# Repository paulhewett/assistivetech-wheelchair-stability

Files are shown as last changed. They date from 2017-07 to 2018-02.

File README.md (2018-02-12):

## Wheelchair Static Stability Test Rig

This system can be sued to measure wheelchair static stability. The design's being published to allow better community development and feedback.

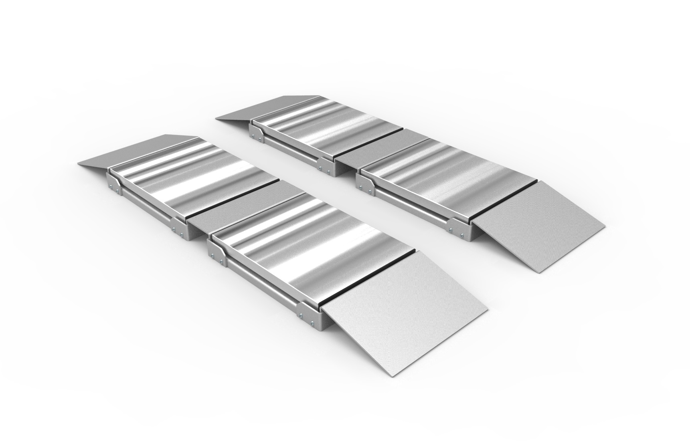
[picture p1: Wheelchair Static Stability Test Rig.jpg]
Wheelchair Static Stability Test Rig


You can use [these pages to see the instructions and to calculate theoretical stability](https://paulhewett.github.io/wheelchair-static-stability-test-rig/) based on scale measurement data.

I've currently just posted a version developed some years ago, with a view to some development soon. It is still a work in progress, so do bear with!

The hardware design will be published, and is similar to the version shown in the photos. We are currently working with digital scales, and I do use the calculation form.

If you do use it, you will need to establish your own protocol for best practice. The formulae used need checking, so check them first before you rely on them. 

Also see these two related repositories:

https://github.com/ACECentre/MAT-doc

https://github.com/ACECentre/Wheelchair-Stability-App

Development is happening now, so get in touch or add issues to feed into this project. Thanks!

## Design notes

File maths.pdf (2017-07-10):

WHEELCHAIR STABILITY MEASUREMENT SYSTEM

Considering the diagram below to find the total weight:

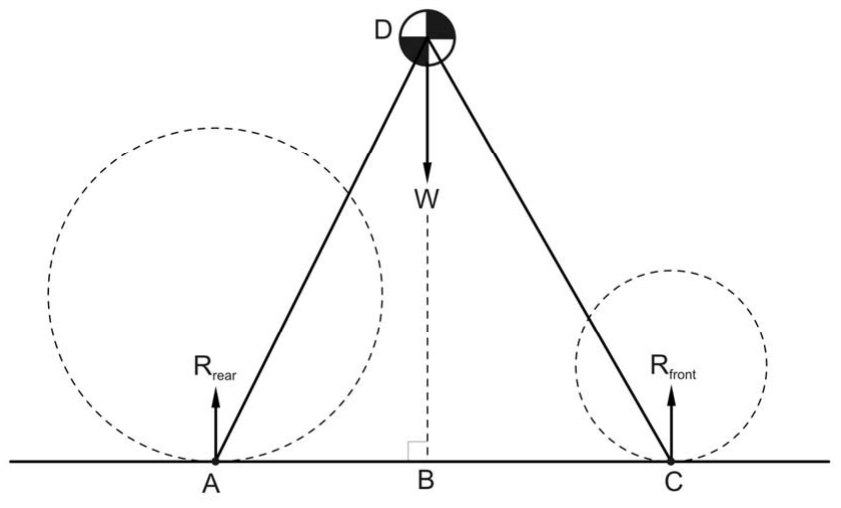
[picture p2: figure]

Rrear = Massrear x 9.81

Rfront = Massfront x 9.81

W = Rrear + Rfront

Considering the following diagram:

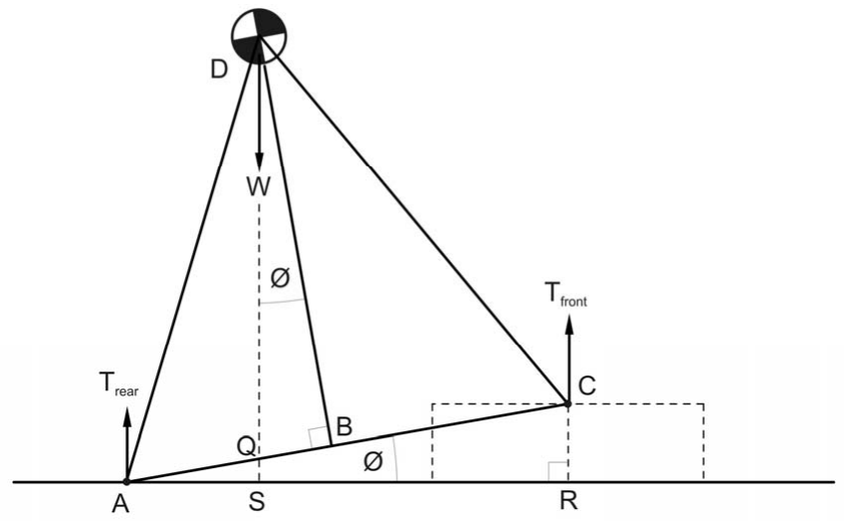
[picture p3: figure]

Taking moments about A to find AB:

AB x W = AC x Rfront

AB = (AC x Rfront) / W

Also,

sin ø = CR/AC

ø = arcsin (CR/AC)

The mass on one pair of wheels is measured to provide an angle of tip.

Tfront = Mfront x 9.81

To find AR:

cos ø = AR/AC

AR = AC x cos ø

Taking moments about A to find AS:

AS x W = AR x Tfront

AS = (AR x Tfront) / W

To find AQ:

cos ø = AS / AQ

AQ = AS / cos ø

To find BQ:

AB = AQ + BQ

BQ = AB – AQ

To find BD:

tan ø = BQ / BD

BD = BQ / tan ø

Consider the following diagram to find the tip and the maximum kerb height

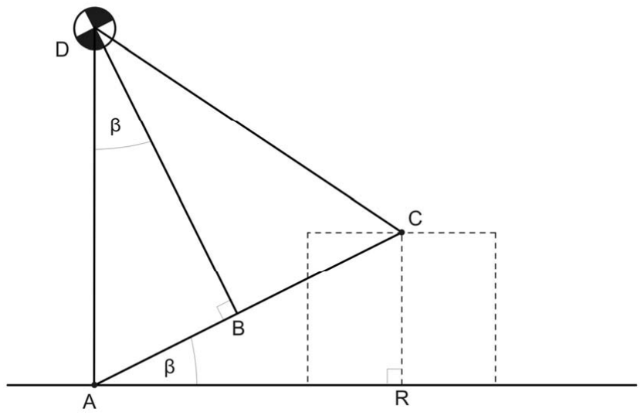
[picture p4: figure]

To find the angle of tip in a rearward direction:

tan β = AB / BD

β = arctan (AB / BD)

To find maximum height of kerb:

sin β = CR / AC

CR = AC sin β

To find the angle of tip in a forward direction:

tan δ = BC / BD

δ = arctan (BC / BD)

To find the maximum height of kerb:

sin δ = AR / AC

AR = AC sin δ

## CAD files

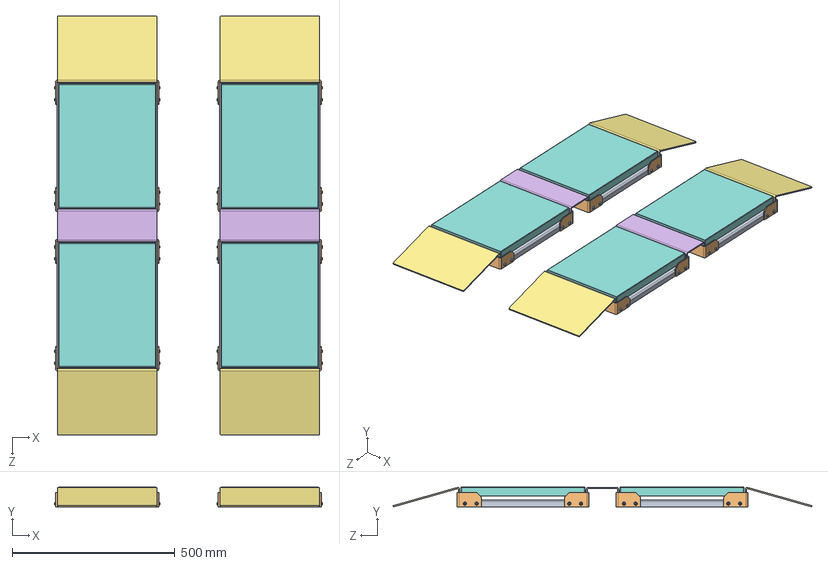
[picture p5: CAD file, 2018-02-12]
CAD/303-001 Test Rig Assembly/303-001-001 Test Rig Asembly.SLDASM
824.6 x 61.0 x 1288.2 mm
M6x16 Allen Button Head Screw x 32
M6 Washer Plain x 32
Nyloc Nut x 32
Salter WS120 Scales x 4

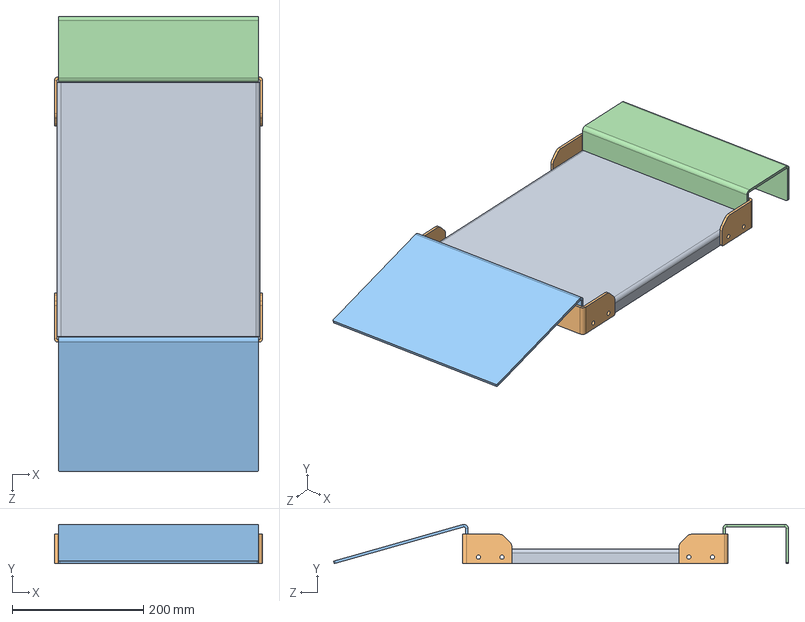
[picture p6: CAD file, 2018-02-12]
CAD/303-005 Assembly/303-005-001.SLDASM
318.0 x 60.0 x 694.1 mm

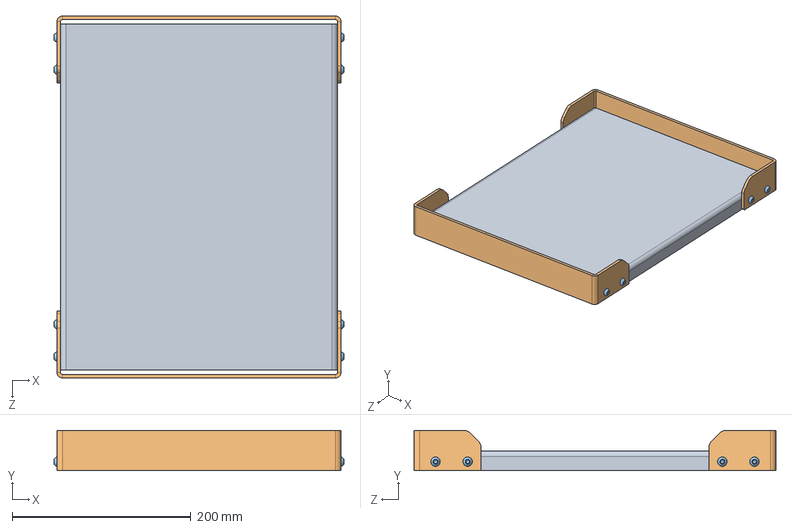
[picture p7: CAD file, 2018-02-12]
CAD/303-005 Assembly/303-005-002.SLDASM
324.6 x 45.0 x 405.0 mm
M6x16 Allen Button Head Screw x 8
M6 Washer Plain x 8
Nyloc Nut x 8

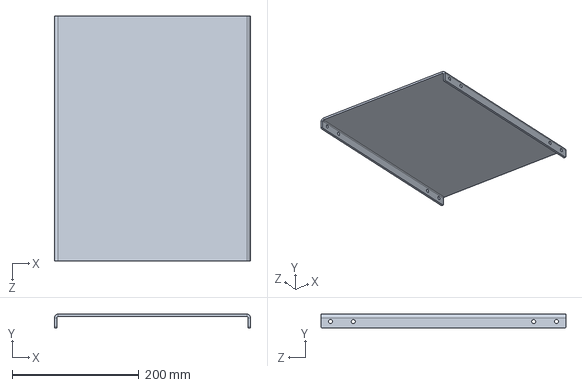
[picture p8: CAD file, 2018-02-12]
CAD/303-002 Scale Platform/303-002-001.SLDPRT
310.0 x 22.0 x 387.0 mm

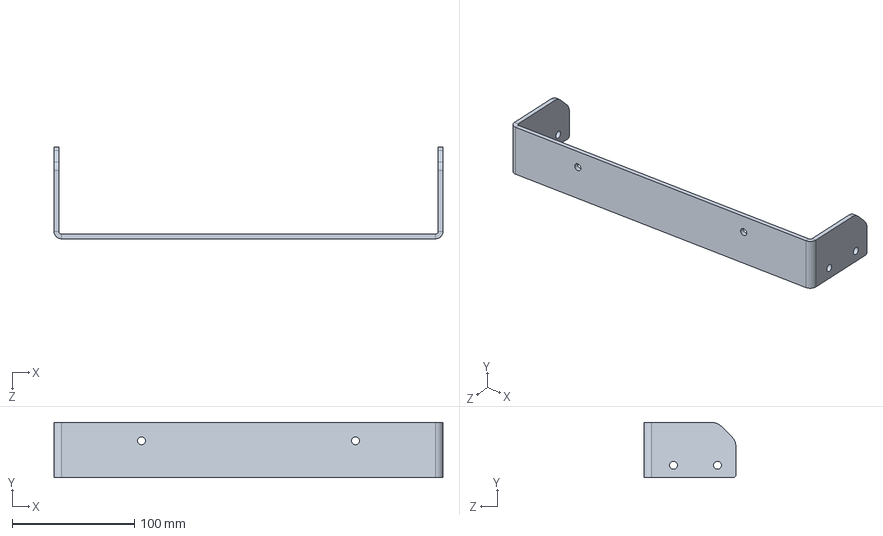
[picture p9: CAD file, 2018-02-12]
CAD/303-003 End Guide/303-003-001.SLDPRT
318.0 x 45.0 x 75.0 mm

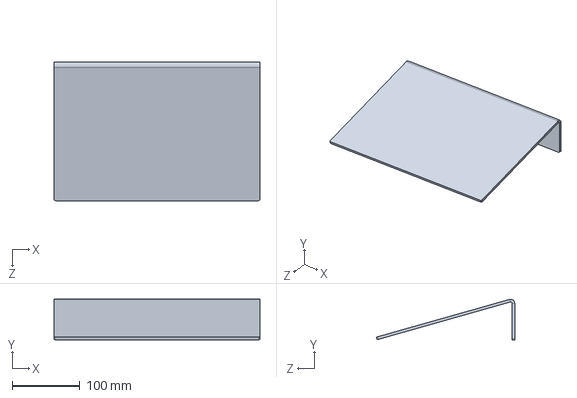
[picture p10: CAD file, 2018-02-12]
CAD/303-004 Ramp/303-004-001.SLDPRT
305.0 x 60.0 x 205.1 mm

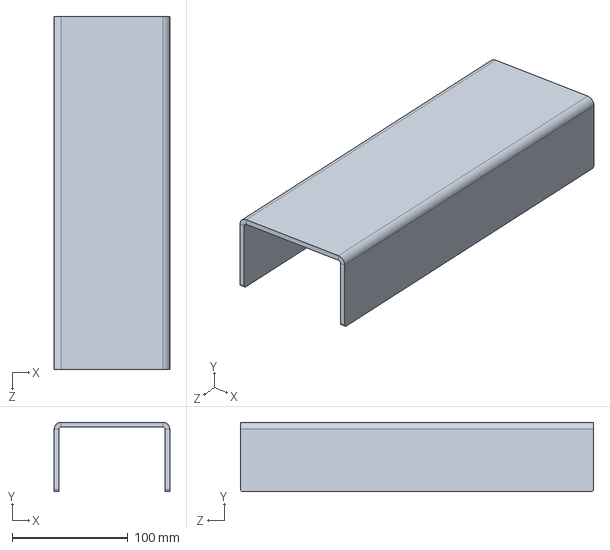
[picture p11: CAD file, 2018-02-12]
CAD/303-006 Spacer Plate/303-006-002.SLDPRT
100.0 x 60.0 x 305.0 mm

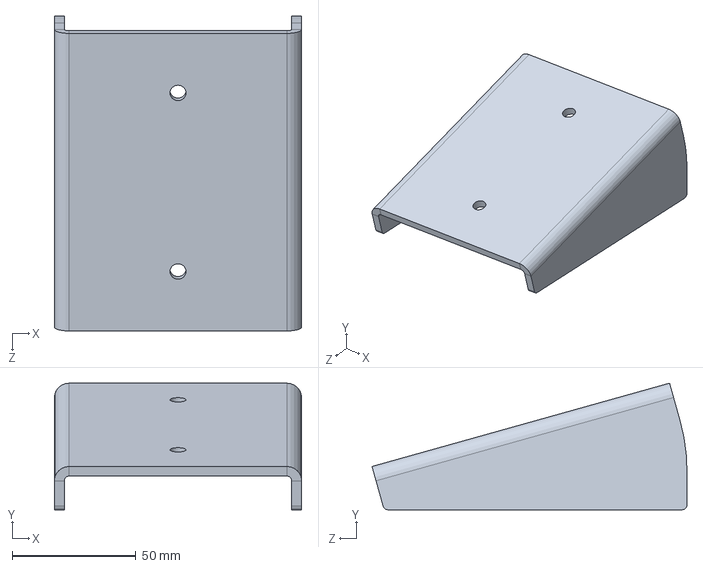
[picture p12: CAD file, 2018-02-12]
CAD/303-007 Ramp Support/303-007-001.SLDPRT
100.0 x 51.2 x 127.4 mm

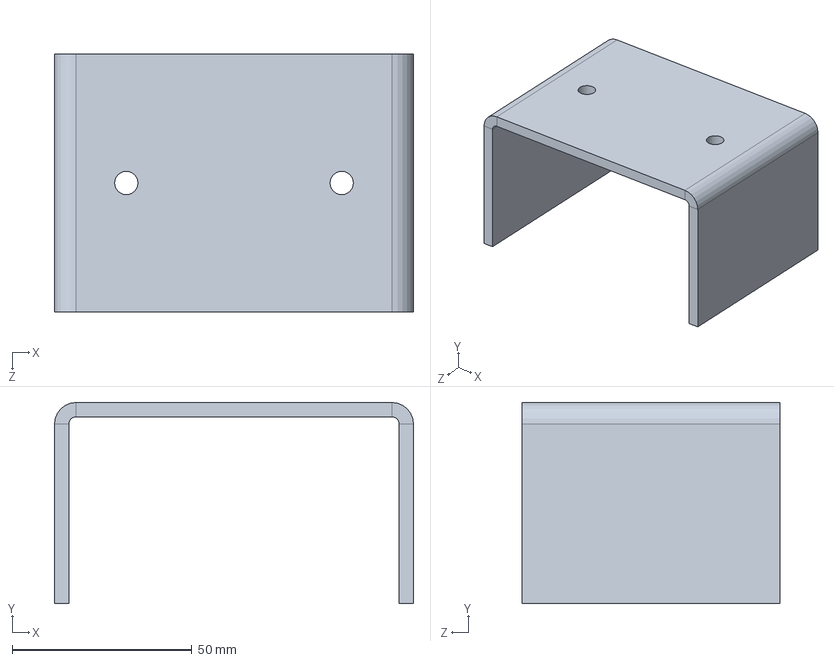
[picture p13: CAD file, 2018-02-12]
CAD/303-008 Support Plate/303-008-001.SLDPRT
100.0 x 56.0 x 72.0 mm

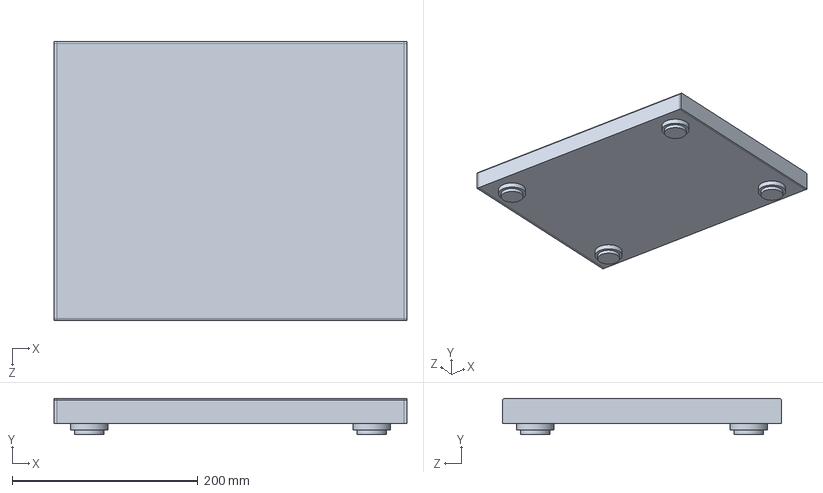
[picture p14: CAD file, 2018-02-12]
CAD/_parts/Salter WS120 Scales.SLDPRT
380.0 x 39.0 x 300.0 mm

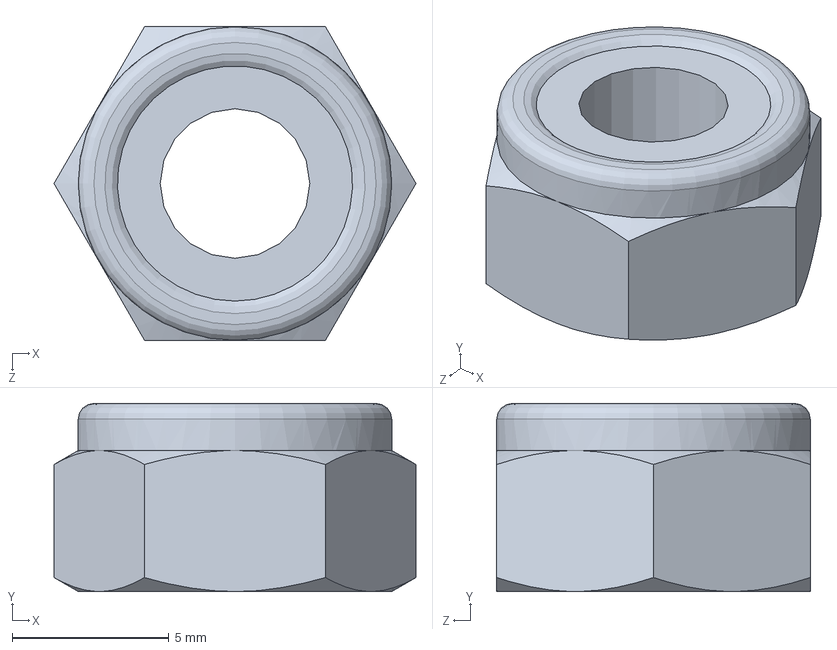
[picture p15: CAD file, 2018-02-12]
CAD/_parts/Nyloc Nut.SLDPRT
11.5 x 6.00 x 10.0 mm

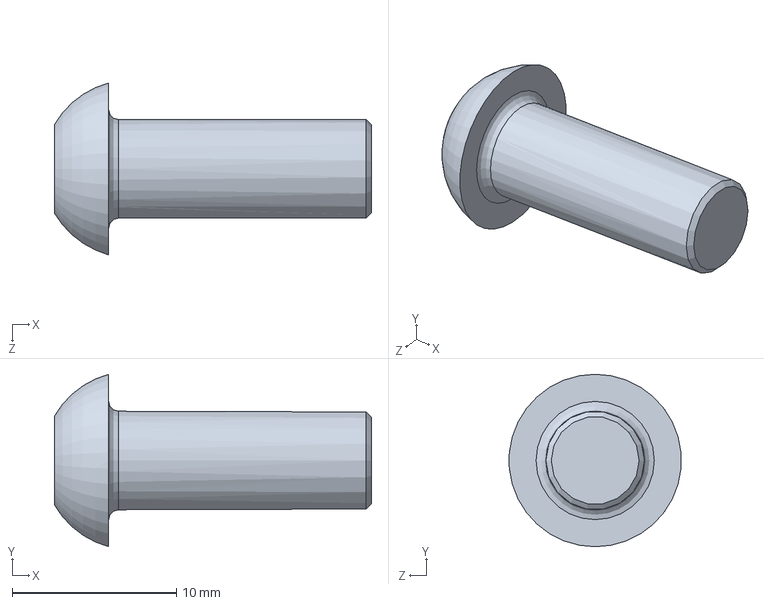
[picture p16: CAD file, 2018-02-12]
CAD/_parts/M6x16 Allen Button Head Screw.SLDPRT
19.3 x 10.5 x 10.5 mm

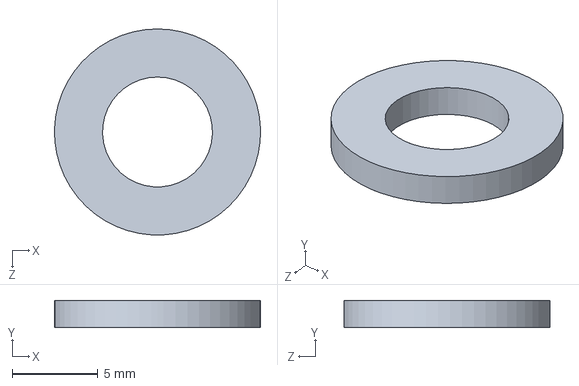
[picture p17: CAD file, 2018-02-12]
CAD/_parts/M6 Washer Plain.SLDPRT
12.0 x 1.60 x 12.0 mm

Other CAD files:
CAD/303-003 End Guide/303-003-002.SLDPRT
CAD/303-004 Ramp/303-004-002.SLDPRT
CAD/303-006 Spacer Plate/303-006-001.SLDPRT
CAD/303-002 Scale Platform/303-002-001.DXF
CAD/303-002 Scale Platform/303-002-001.SLDDRW
CAD/303-002 Scale Platform/303-002-001.STL
CAD/303-003 End Guide/303-003-001.DXF
CAD/303-003 End Guide/303-003-001.SLDDRW
CAD/303-003 End Guide/303-003-001.STL
CAD/303-004 Ramp/303-004-001.DXF
CAD/303-004 Ramp/303-004-001.SLDDRW
CAD/303-004 Ramp/303-004-001.STL
CAD/303-005 Assembly/303-005-001.SLDDRW
CAD/303-006 Spacer Plate/303-006-001.DXF
CAD/303-006 Spacer Plate/303-006-001.SLDDRW
CAD/303-006 Spacer Plate/303-006-001.STL
CAD/303-007 Ramp Support/303-007-001.DXF
CAD/303-007 Ramp Support/303-007-001.SLDDRW
CAD/303-007 Ramp Support/303-007-001.STL
CAD/303-008 Support Plate/303-008-001.DXF
CAD/303-008 Support Plate/303-008-001.SLDDRW
CAD/303-008 Support Plate/303-008-001.STL

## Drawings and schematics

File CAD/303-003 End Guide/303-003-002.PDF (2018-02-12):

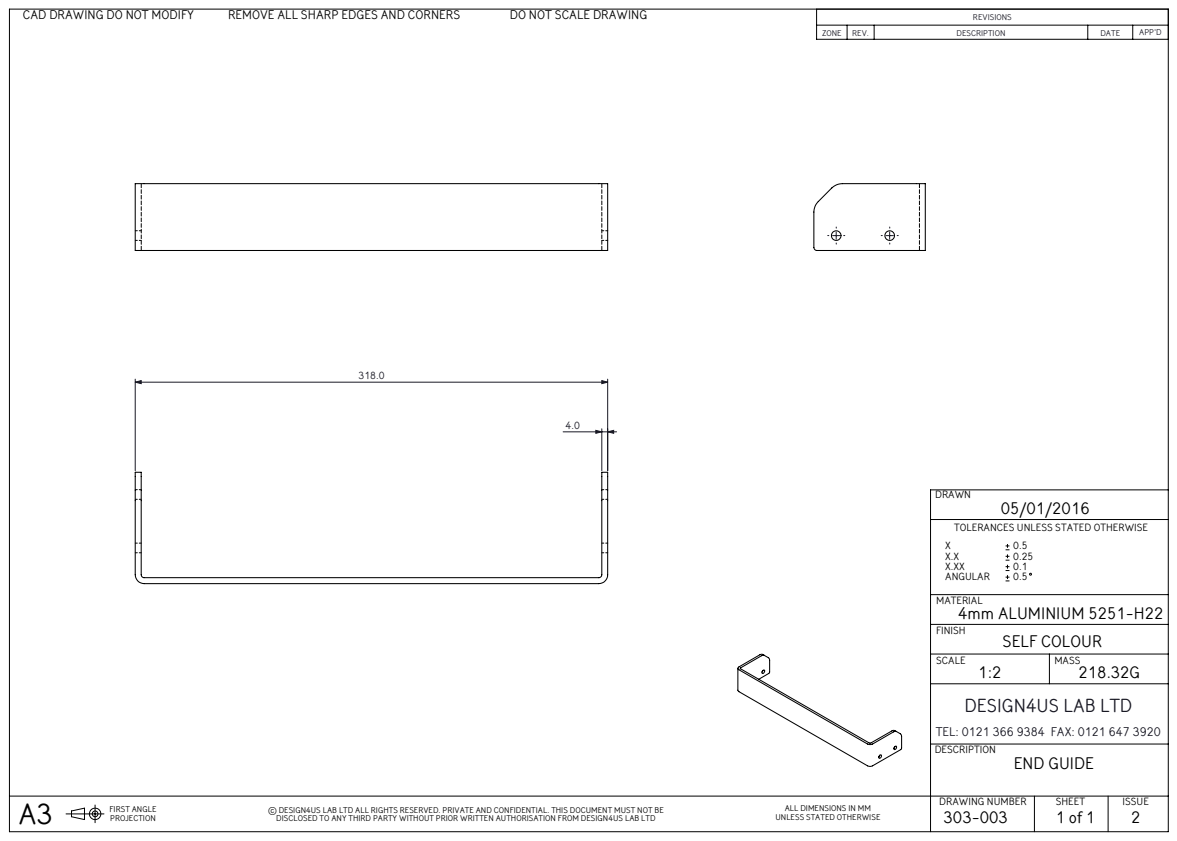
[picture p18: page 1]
FIRST ANGLE; END GUIDE; DRAWING NUMBER; SELF COLOUR; TOLERANCES UNLESS STATED OTHERWISE; 4mm ALUMINIUM 5251-H22; CAD DRAWING DO NOT MODIFY; REMOVE ALL SHARP EDGES AND CORNERS; DO NOT SCALE DRAWING; DESIGN4US LAB LTD; TEL: 0121 366 9384 FAX: 0121 647 3920

© DESIGN4US LAB LTD ALL RIGHTS RESERVED. PRIVATE AND CONFIDENTIAL. THIS DOCUMENT MUST NOT BE
DISCLOSED TO ANY THIRD PARTY WITHOUT PRIOR WRITTEN AUTHORISATION FROM DESIGN4US LAB LTD

ALL DIMENSIONS IN MM
UNLESS STATED OTHERWISE

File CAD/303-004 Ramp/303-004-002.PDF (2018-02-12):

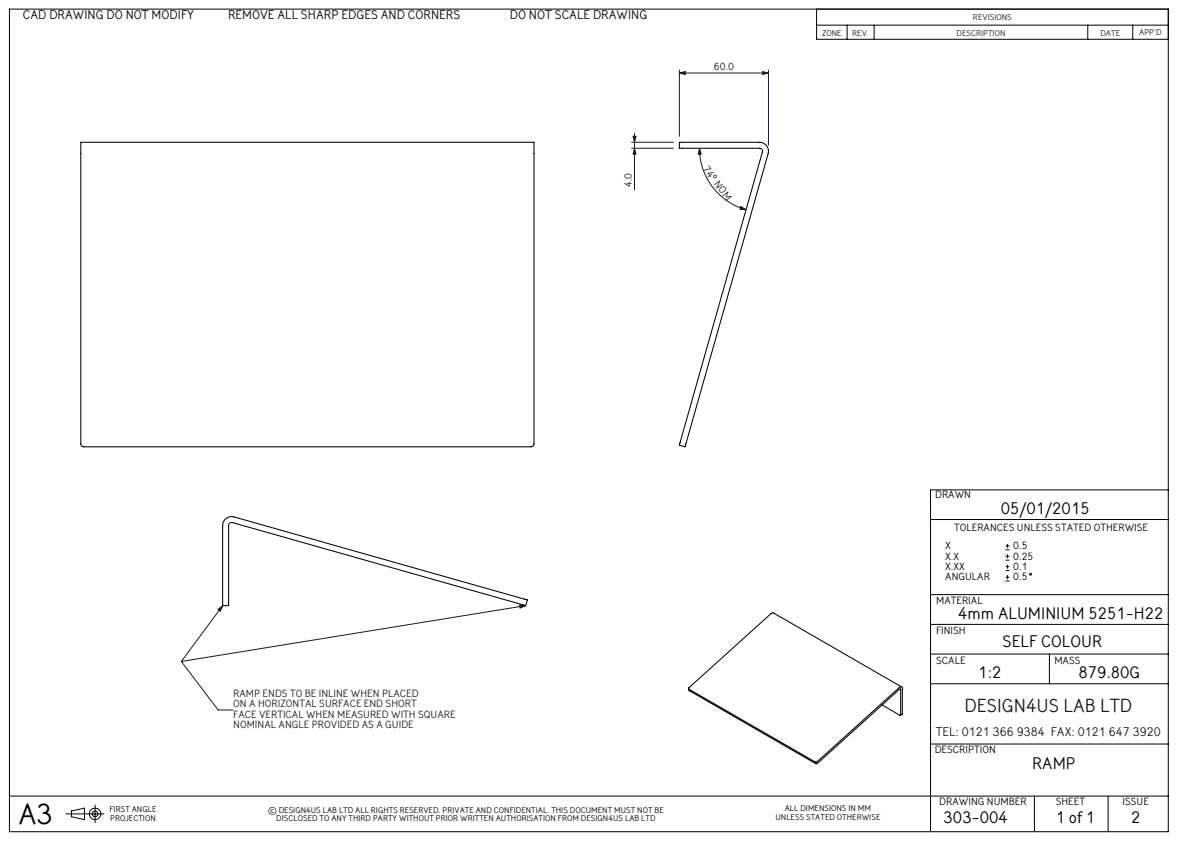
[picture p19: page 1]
74° NOM; FIRST ANGLE; DRAWING NUMBER; SELF COLOUR; TOLERANCES UNLESS STATED OTHERWISE; 4mm ALUMINIUM 5251-H22; CAD DRAWING DO NOT MODIFY; REMOVE ALL SHARP EDGES AND CORNERS; DO NOT SCALE DRAWING; DESIGN4US LAB LTD; TEL: 0121 366 9384 FAX: 0121 647 3920

RAMP ENDS TO BE INLINE WHEN PLACED
ON A HORIZONTAL SURFACE END SHORT
FACE VERTICAL WHEN MEASURED WITH SQUARE
NOMINAL ANGLE PROVIDED AS A GUIDE

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

ALL DIMENSIONS IN MM
UNLESS STATED OTHERWISE

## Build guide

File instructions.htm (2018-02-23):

# Measuring the force on the wheels

1) Position the ramps on a level surface, with the scales located in the ramp section. Push the wheelchair onto the scales so the castors are centrally aligned on the top surface of the scales. Record the value shown by the scales for both the left and right castors.

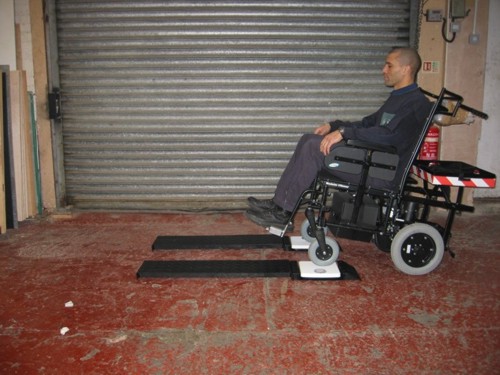
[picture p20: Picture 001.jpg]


2) Push the wheelchair forwards so the rear wheels are positioned centrally on the scales. The casotrs will be located at some point on the flat surface of the ramp.

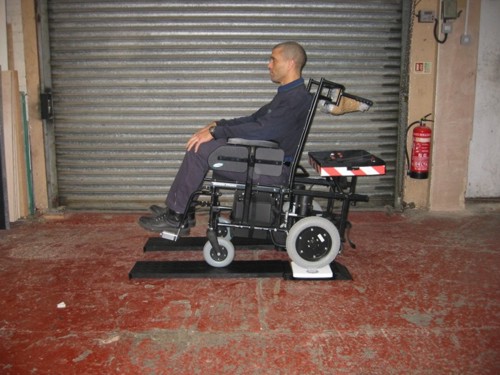
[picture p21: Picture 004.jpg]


3) Push the wheelchair forwards so it is fully on the flat surface of the ramps. Engage the wheelchair brakes, and move the ramps from the rear to the front of the wheelchair.

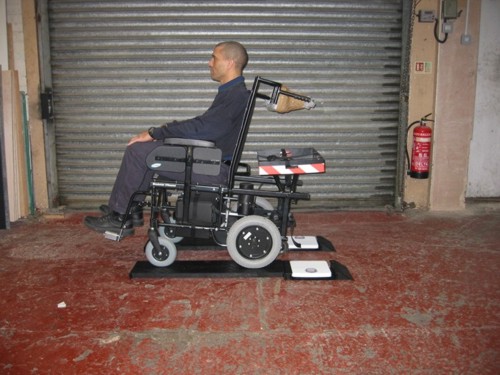
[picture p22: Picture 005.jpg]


4) Push the wheelchair forwards so the castors are centrally located on the scales. Record the measurements.

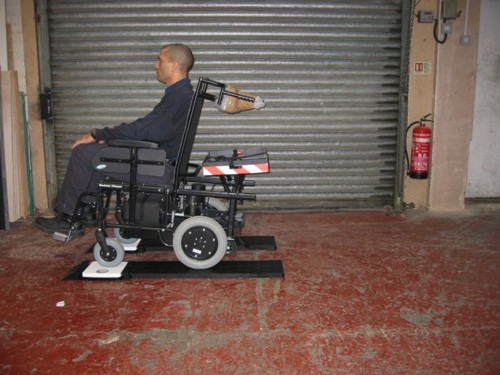
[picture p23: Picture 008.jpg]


5) All measurements have now been taken. The wheelchair can be taken off the ramps.

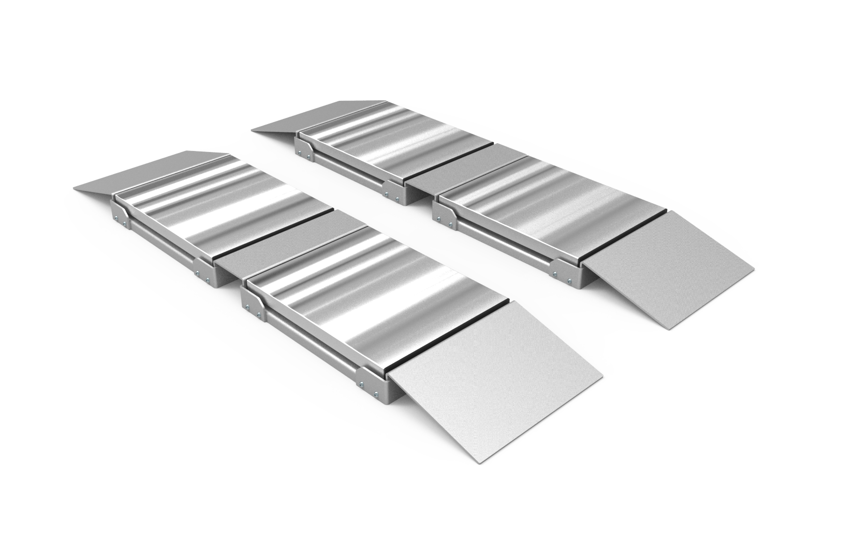
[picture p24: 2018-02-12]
CAD/303-001 Test Rig Assembly/303-001 Test Rig Assembly D.png

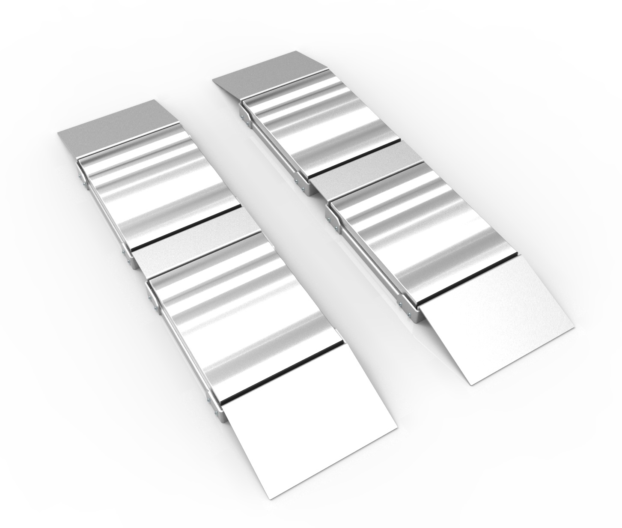
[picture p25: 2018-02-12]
CAD/303-001 Test Rig Assembly/303-001 Test Rig Assembly B.jpg

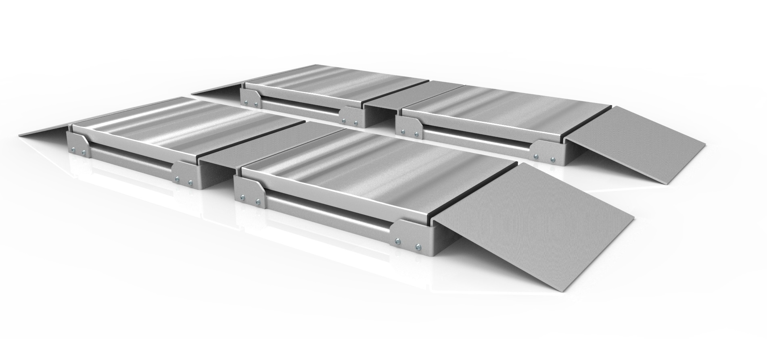
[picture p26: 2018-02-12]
CAD/303-001 Test Rig Assembly/303-001 Test Rig Assembly C.jpg

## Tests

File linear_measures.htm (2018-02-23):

# Taking the linear dimensions of the wheelchair

This can be done in two ways:

1. Measure the wheelbase of the wheelchair
2. Measure the dimensions shown below, and use the 'Calculate Wheelbase' button in the data form. As it is easier to more accurately measure the dimensions shown in the figure below and calculate the wheelbase, this would be the preferred way and is likely to reduce measurement error.

This should be done with the castor positioned as if the wheelchair is being pushed forwards (as in the photo, not as in the diagram).

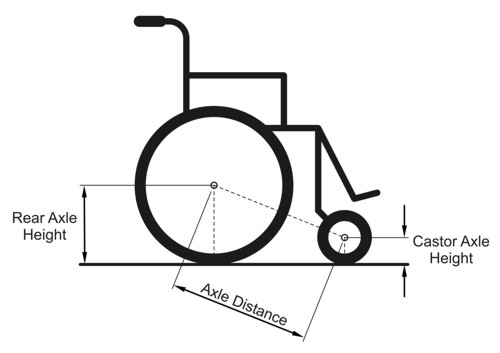
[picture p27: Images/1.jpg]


1) Measure the Rear Axle height. This must be the vertical distance from the floor to the centre of the axle.

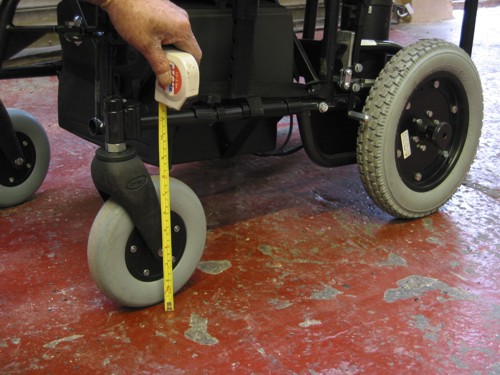
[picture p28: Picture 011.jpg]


2) Measure the Front Axle height. This must be the vertical distance from the floor to the centre of the axle.

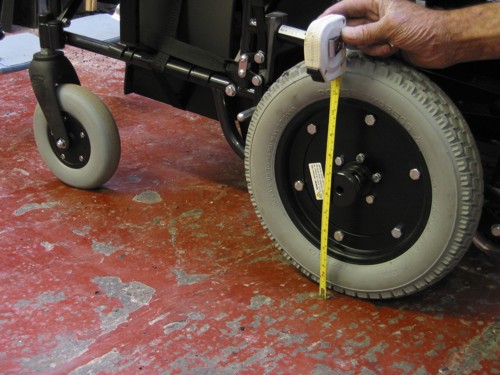
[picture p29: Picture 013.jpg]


3) Measure the distance between the centres of the front and rear axles.

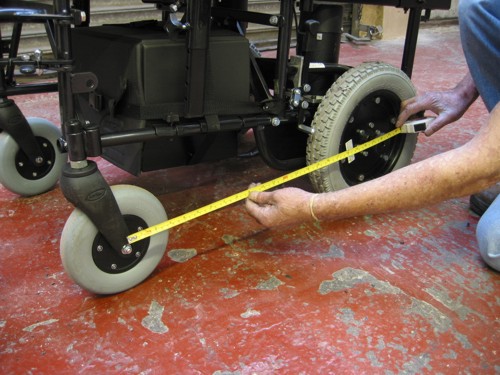
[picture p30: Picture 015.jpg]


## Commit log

2018-02-12 Added CAD files of current design
    [303-002-001.DXF, 303-002-001.SLDDRW, 303-002-001.SLDPRT, 303-002-001.STL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]
2018-02-12 Design updated
    Assembly completed. Render images and stl files of components added.
    [303-001-001 Test Rig Asembly.SLDASM, 303-002-001.SLDPRT, 303-003-001.SLDDRW, 303-003-001.SLDPRT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]
